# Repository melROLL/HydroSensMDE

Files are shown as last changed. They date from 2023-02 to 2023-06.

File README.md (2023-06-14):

# HydroSensMDE

## The TEAM
the team is composed of : Joshua, Tristan, Nicolas and Melvyn

## The Software 
You can download the realease folder in order to have the .exe file for windows and find as well the instruction manual.
all the source code is provided in the technical part if you need or want to compile it for other operating system. 

### user interface 

<p align="center">
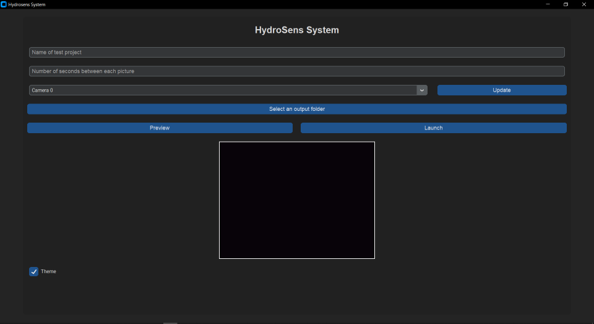
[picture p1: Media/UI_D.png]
  
</p>

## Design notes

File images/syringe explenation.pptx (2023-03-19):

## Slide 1

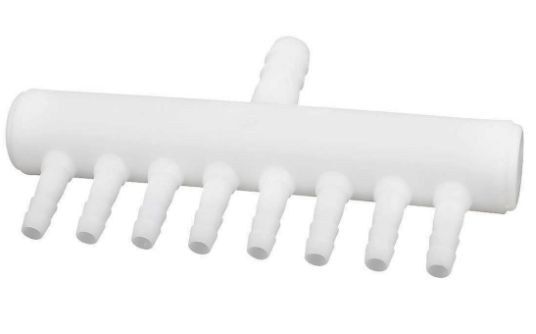
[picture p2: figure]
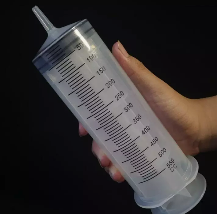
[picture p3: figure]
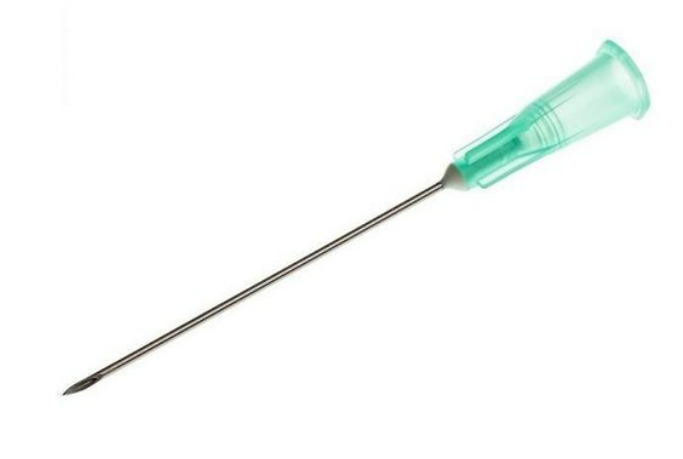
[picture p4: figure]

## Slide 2

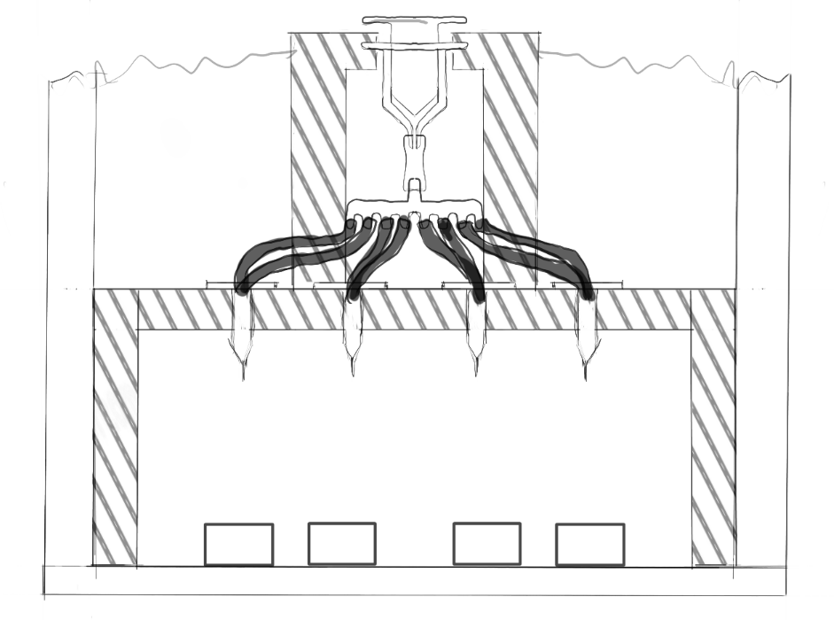
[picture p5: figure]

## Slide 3

product | qty | price
big syringe | 1 | 8,01
tube | 20 cm | 1,99
tubesplitter | 1 | 9,94
syringe needles | 10 | 5,28
wood | scrapwood from school
filament | leftover from the photobox
screws | leftover from the photobox
total | | 25,22

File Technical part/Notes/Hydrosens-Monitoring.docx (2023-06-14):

# Fourth-year project

Participants:

- Joshua GROEN
- Tristan MICHELENA
- Melvyn ROLLAND
- Nicolas WATTENHOFFER

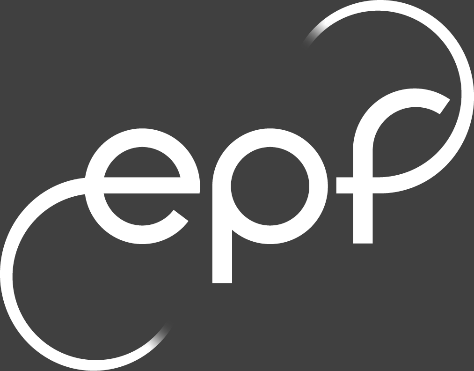
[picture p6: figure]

# Management monitoring

## Context

The client Ms. Mouton makes a lot of experiments testing different products from her subject study. She follows a protocol, and she takes pictures of the results. She visualizes the absorption of the water on a treat piece of paper regarding the duration. The point is today, everything is made by hand. These experiments require a lot of precious time of Ms. Mouton. The main point of this project is to automatize these steps following the same protocol. The project is spliced in two parts. The first part concerns the physical tools necessary to automatically take pictures in repeatable environment. The second part treats the development of the software to detect when the product fails.

## Objectives

Criteria of Ms. Mouton:

- Easy user interface
- Time saving.

Criteria for the consistency and the usage of the project:

- Make the experiment repeatable, same samples, same results:
  - Same environment
  - Fixed position of the camera and same lighting condition
  - Fixed position of the sample
- Usage guide

Functionalities:

1. Acquire picture every defined time.
2. Once the absorption is detected:
a. Visualize experiment result: at which time absorption occurred.
b. Visualize the flow rate of absorption.
3. Store the results.

## Management tools

- Github
- Teams
- Roadmap and Backlog

## First meeting – Story mapping 02/02/2023.

1. Understand the project of the client.
2. Understand the need of the client.
3. The steps of the project: Design a prototype, create a data processing tool, test and improve.
4. Create something simple of usage.
5. Functionalities:
  - Data output: absorption or not, amount of water, time at which absorption occurred, flow rate.
  - Let the user choose the duration between pictures.
  - Export a csv file with results.
  - Stop the experiment when all samples absorbed.
6. To contact Ms. Mouton, use Teams or in face to face at school.

## Second meeting – Monitoring 02/10/2023.

1. Budget:
- Camera 2k: over 15€
- Use the camera giving but the teacher, Logitech 720p.
- Light: circular light or led -> we can test both.
- Check for wood if we build the box or buy a folding box.
- A budget can be assigned by the school.
2. The box:
- Number of samples: between 4-8 samples.
- Looking for a hydrophobic floor.
3. Program:
- Add a name for the folder of each experiment.

Third meeting – Monitoring 02/17/2023.

We had a meeting without the client Ms. Mouton.

We have decided to share our files via github and we practiced using it. We concluded that we should buy as soon as possible everything we need, and we also have a camera from Mr. Gademer.

To do for next time:

- Create the list of tasks regarding the roadmap.
- Search ideas for the floor box.
- Ask Cyril Durant if we can get the wood to establish the budget.
- Presentation: Why do we want to build the box ourselves? And the budget.
- Create a report of last week meeting.
- Create the list of tasks regarding the roadmap.

## Fourth meeting – Monitoring 02/24/2023.

News

How to put water droplets on all the samples on the same time? (With an acceptable delay of 10 seconds).

According to the meeting this morning. We will reduce the number of samples to a maximum of 4. Indeed, the amount of water put on the paper is very precise and need a pipette to be realized.

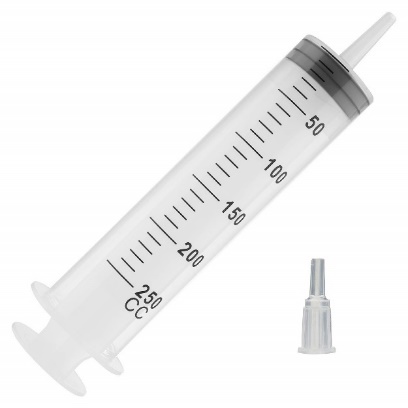
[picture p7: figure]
250ml Syringe, Extra Large Plastic Syringes for Glue Dispensing, Scientific Labs, Watering, Refilling, Multiple Uses: Amazon.com: Industrial & Scientific

In a second time we can think about a system which can facilitate the experiment’s process. The two possibilities are the software method, in other words put sample one after the other. Second possibility, to create an easy-to-use support as showed by the following pictures:

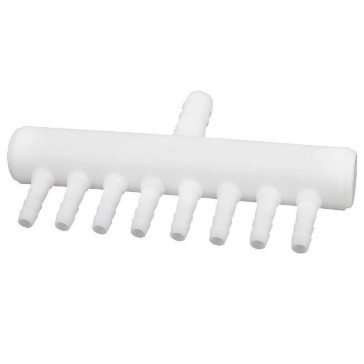
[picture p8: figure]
Plastic 8-Way Aquarium Tube Splitter Air Valve - Walmart.com
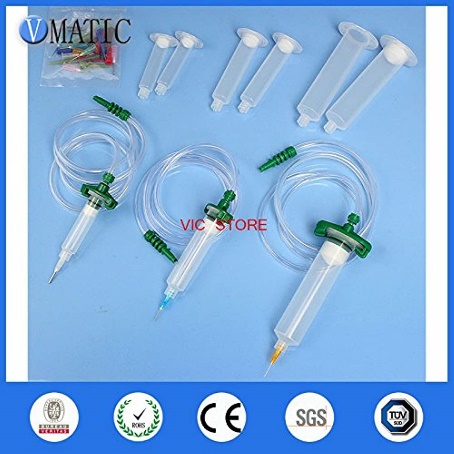
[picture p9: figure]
Liquid Dispensing Adhesive Glue Plastic Pneumatic Syringe + Dispenser Syringe Adapter Fitting Valve 5/10/30 Cc Ml + Syringe Needles: Amazon.com: Industrial & Scientific

We propose two possibilities for the floor of the box:

- Plastic cotenant, to buy.
- Acrylic panel, to build.

Decisions

We will make the box by ourselves with wood.

To do in a short term:

Ask Cyril Durant for the wood to start the construction of the box.

The next meeting will take place the 03/10/2023 at 9:45 a.m., if we don’t have enough news, we can push the meeting for the next week.

## Fifth meeting – Monitoring 03/10/2023.

### Management meeting

1. The road map.

The road map’s big steps must include a title that represents a deliverable. It’s important to precise that dates are just hypothetical because it’s almost impossible to have a vision of the work so early in the project.

2. Backlog

The tool must be shared with all the participants of the project to make it dynamic. We must create a Kanban board to visualize the progress of the work.

Example:

Backlog | To do | Doing | Done
Box | | | Get the wood
| Cut the wood

The main purpose of the Kanban is to update it every week to highlight the progress compared to the previous meeting. It also involves the client in the monitoring of the tasks.

### Client meeting

1. The water drop solution:

It can resolve the issue; Ms. Mouton will check for materials that allow to implement the solution in the lab.

In all the cases, it’s not an expensive solution. We can test the implementation of the solution.

2. Sample of pictures

Picture name = Number of carbon chain – Dilution – minutes (example= C12-5-2)

3. Fully transparency box

The documentation must be understandable for everyone who don’t know anything about the project with a granularity of the construction of the box, for the physical part. The code will be commented and detailed about the functions for any other people who want to discover it.

The next meeting will take place the 03/24/2023 at 9:45 a.m., if we don’t have enough news, we can push the meeting for the next week.

## Sixth meeting – Monitoring 03/24/2023.

### Management meeting

The roadmap is now well, the previous errors have been corrected. For big changes, it is important to keep the previous version of the roadmap to visualize the difference between the original basis and the actual basis.

More details about the user stories have been given, the user stories are kind of functionalities that have been implemented. The granularity is between the goal of the sprint and the technical tasks.

We are using two different sharing tools, the first one, the kanban model for the customer and the second one, for the teams. This solution is great, the information shared between the team members is not the same that the information shared this the client. However, the tool used by the team members must be more detailed in the planification.

The kanban model must include only the ToDo of the sprint. The point here is to show at the end of the sprint that the defined ToDo at the beginning of the sprint have been made.

### Client meeting

1. Drop water system.

The products to try the water droplets dispenser are ordered and will arrive around the sixth of April. And the precision pipet is in Ms. Mouton office so we can try it.

2. Light.

First, the team want to use strip led. The solution is easier to implement and is also cheaper than a light bulb.

Second, we must check the available part at school and if there is nothing that can help use, Ms. Mouton will buy the article we will propose her.

The next meeting will be the mid-term meeting and will take place the 04/07/2023 at 12:15 a.m.

## Midterm Presentation – Monitoring 04/07/2023.

Feedback and global remark on the project’s organization and work.

Remark

Clear idea visually of project in the beginning

Faced challenges:

- How managed?
- how did we go managed?

Density of pixels different between position?

Different success criteria: not fix.

Consistance of schéma

Use Consistancy to explain where we are:

Show itérative : Validation

Doubt water dop dispenser

## Seventh meeting – Monitoring 04/14/2023.

### Management meeting

The organization of the sprint is now established thanks to the Github project’s tool. It allows to follow all the tasks that must be done during the sprint and to share it with the client. So, this last can follow the advancement of the work.

However, this tool is great for the delivery process and the communication with the client, but we need something else to share the experience team members. Which means how each participant of the work feel about the project. One of the ways to get this feedback is based on emotions. How do I feel working on this project? Am I very motivated or maybe I am disappointed? These feedbacks allow to manage the motivation of the team and to create bands between participants. It is a part of the agile method. This process has nothing to see with the delivery process. For the next meeting, the group must find a way to collect and manage these feedbacks.

The next meeting will be the eighth meeting and will take place the 05/12/2023 at 8:45 a.m.

Joshua GROEN - Tristan MICHELENA - Melvyn ROLLAND - Nicolas WATTENHOFFER 4A Project

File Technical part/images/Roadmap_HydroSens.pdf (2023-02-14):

# Hydrosens

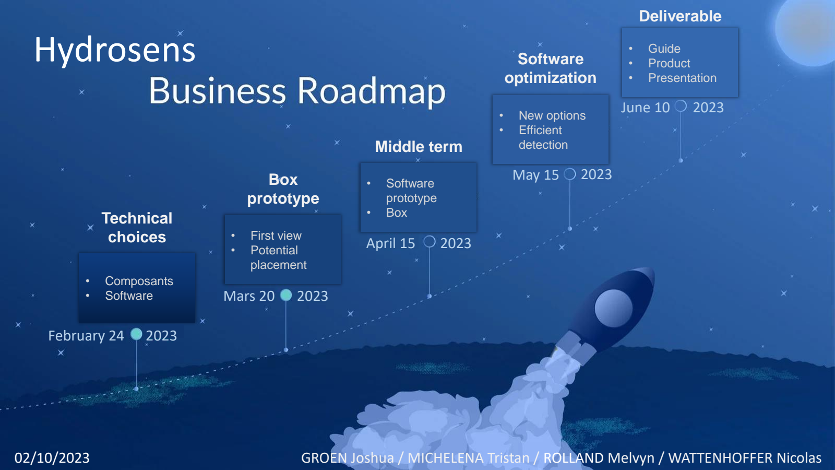
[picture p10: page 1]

- Composants
- Software
- First view
- Potential
placement
- Software
prototype
- Box
- New options
- Efficient
detection
- Guide
- Product
- Presentation
February 24 | 2023
Mars 20 | 2023
April 15 | 2023
May 15 | 2023
June 10 | 2023

Deliverable

Technical
choices

Box
prototype

Middle term

Software
optimization
02/10/2023 | GROEN Joshua / MICHELENA Tristan / ROLLAND Melvyn / WATTENHOFFER Nicolas

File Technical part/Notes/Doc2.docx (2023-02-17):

03/02/2023 meeting with a seminar

During this meeting we discussed what we need to do from the perspective of project manager

We decided to explore how we can make the photo box and present multiple ways to make the box to Julia. In order to make sure we are on the same page and know how to continue.

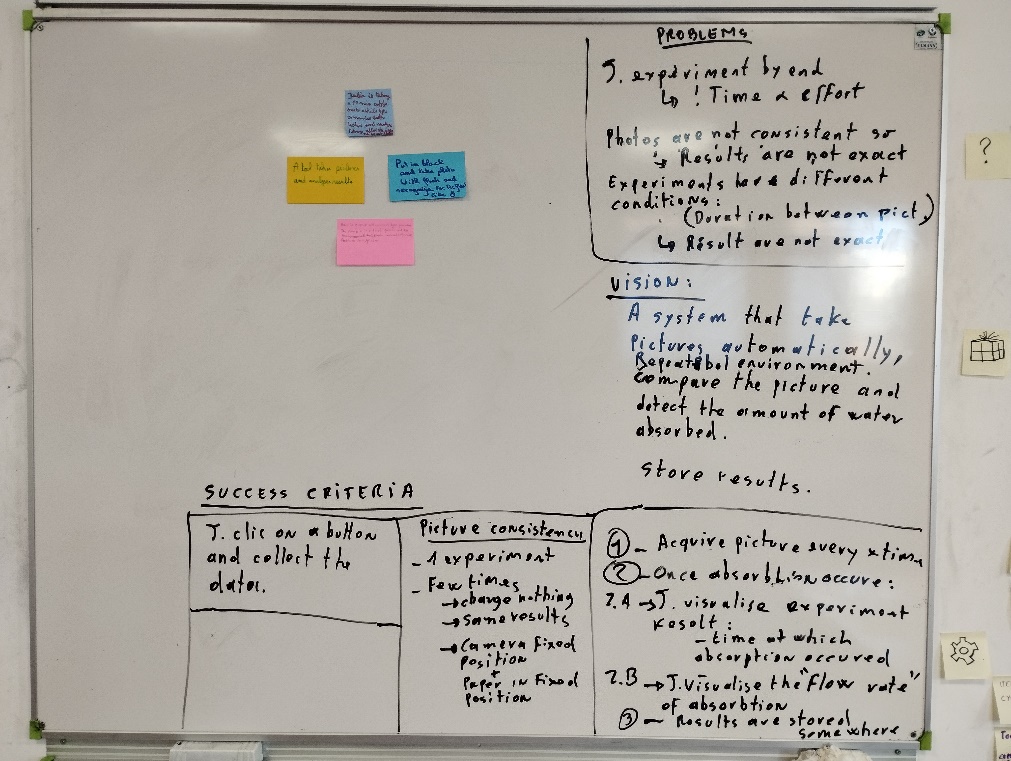
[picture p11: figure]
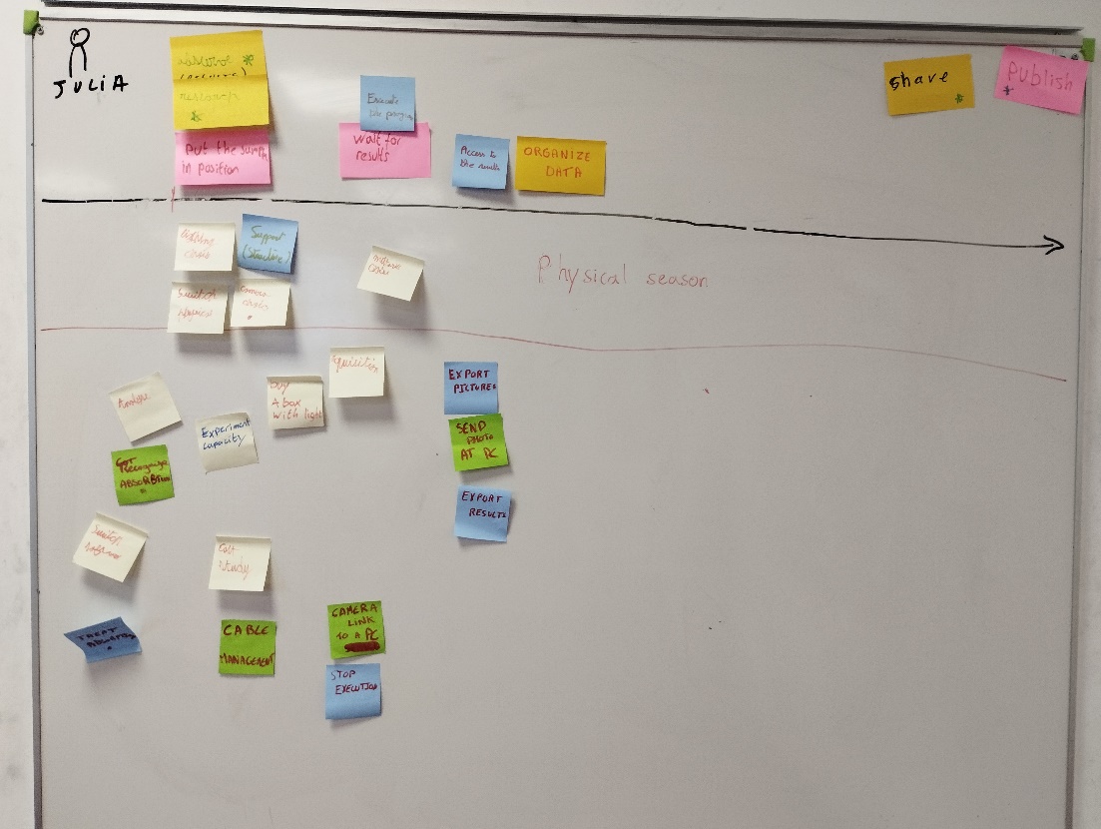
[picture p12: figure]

10/02/2023

We showed our presentation to Julia and came to the conclusion that we have to show her a complete budget of everything we need.

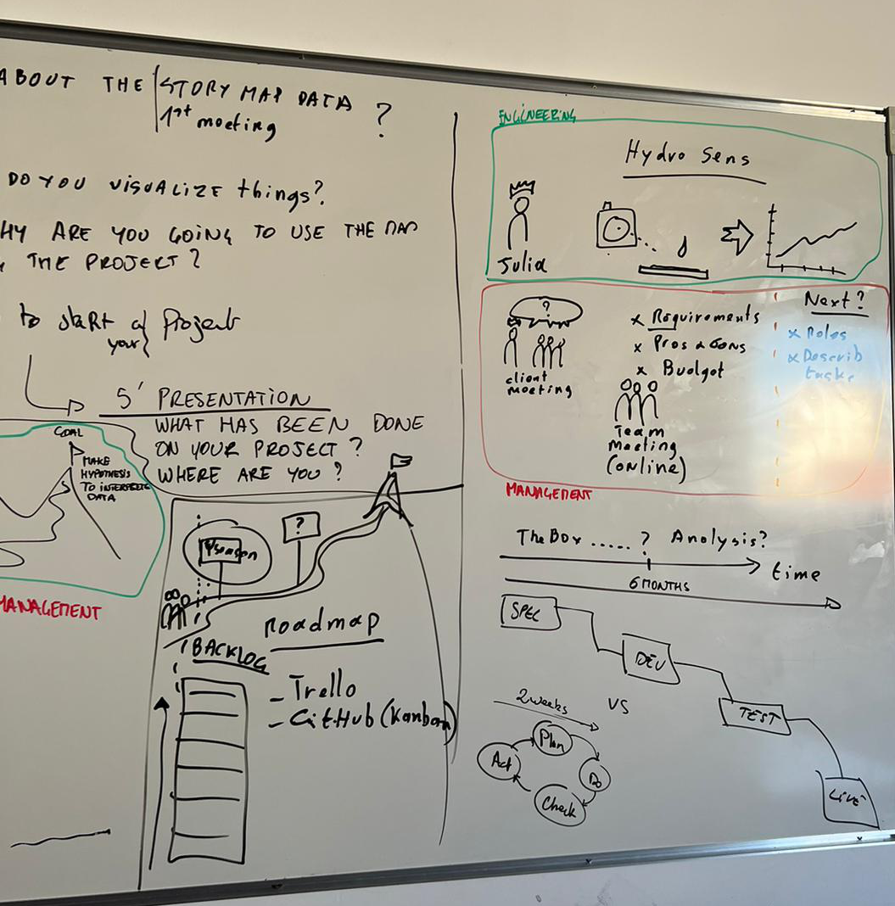
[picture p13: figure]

what we need:

- Argue why we want to make the box ourselves or not
- Create a budget
- Share our notes with everyone involved

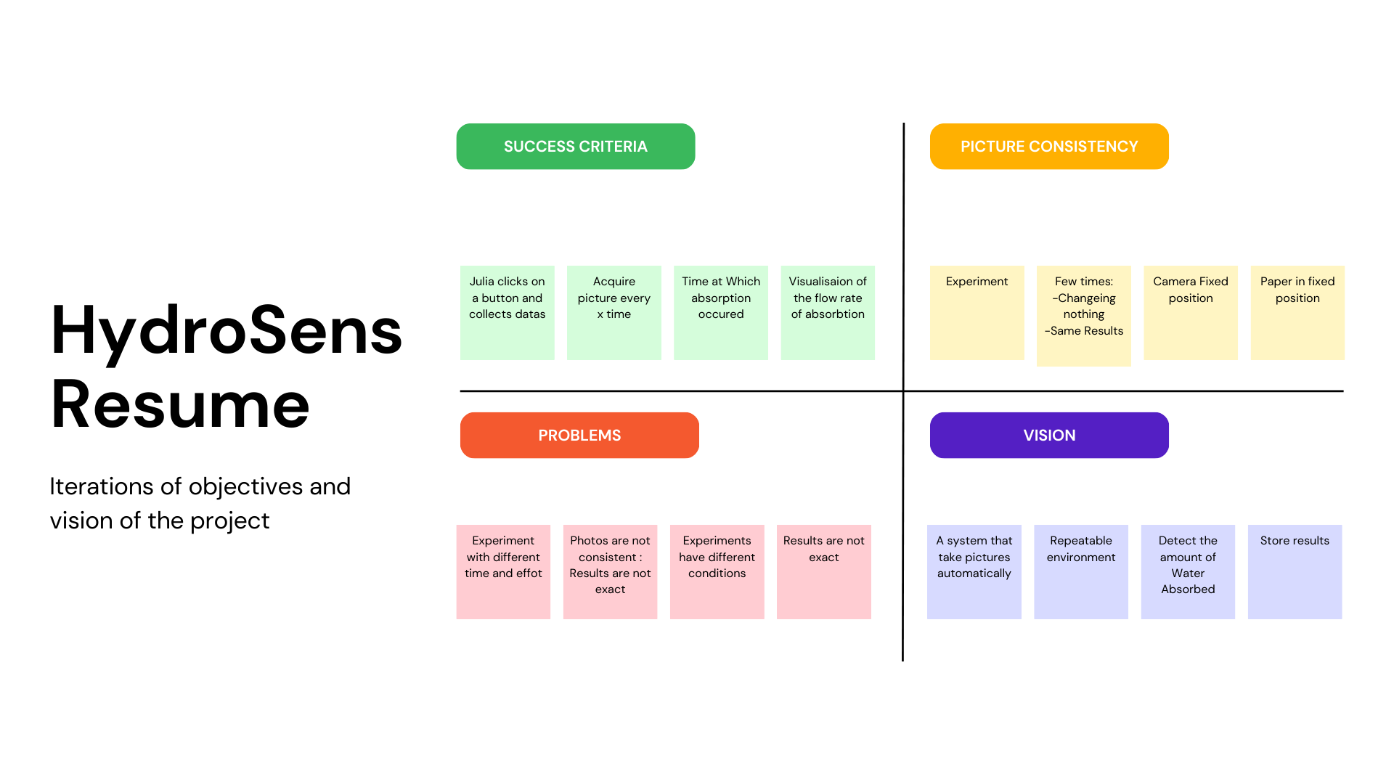
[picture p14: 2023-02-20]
Technical part/images/HydroSens_Resume.png

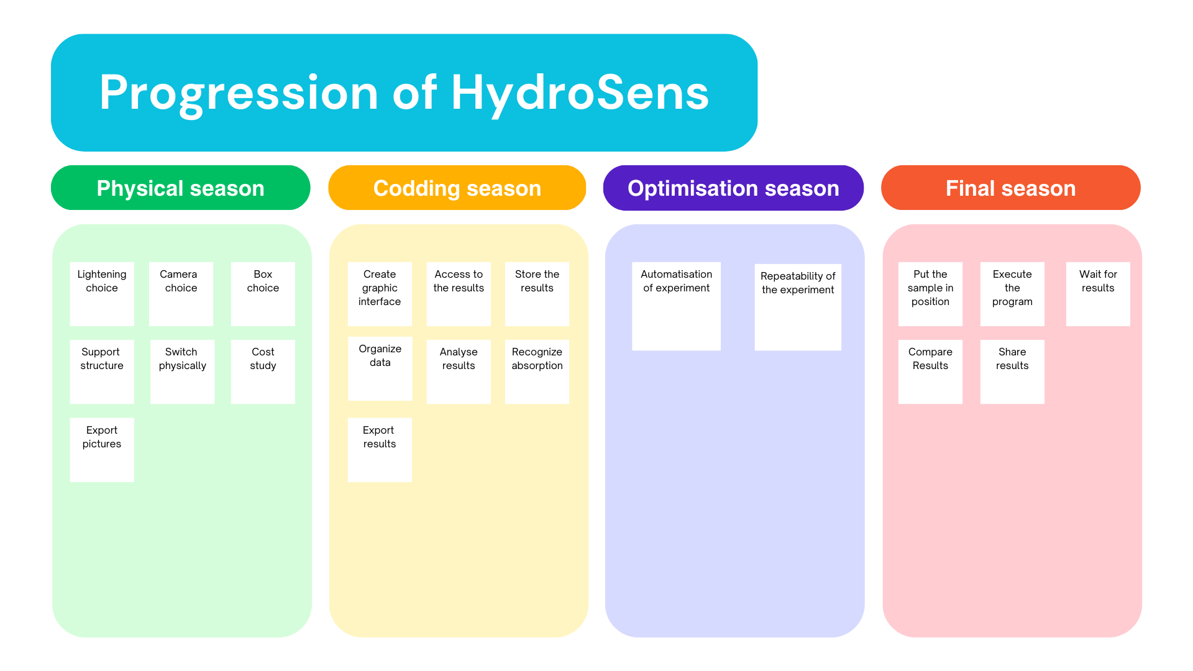
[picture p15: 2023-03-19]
Technical part/images/Plan.png

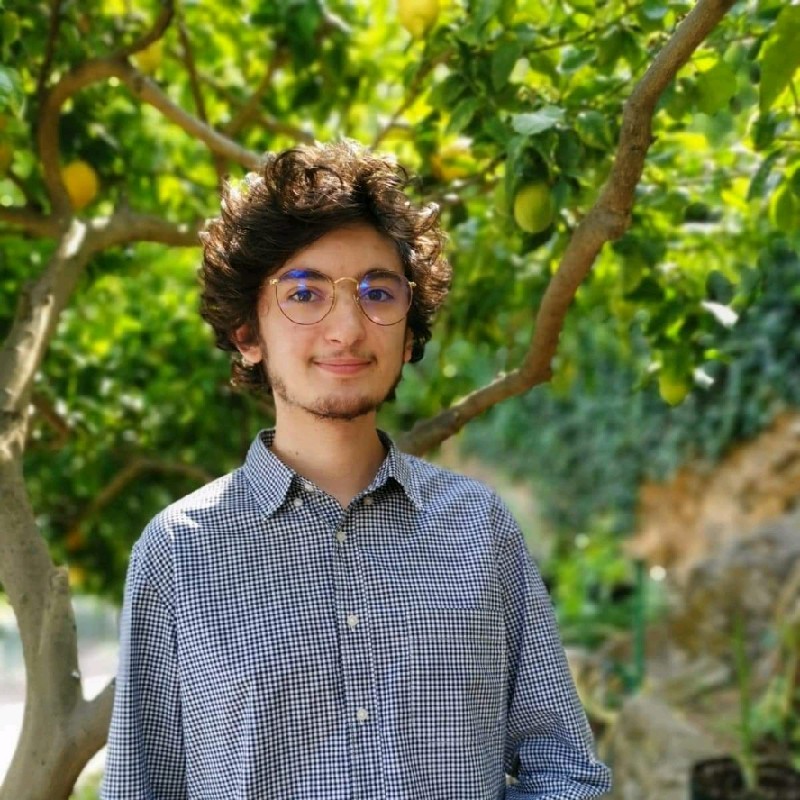
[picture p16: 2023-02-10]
Media/melvyn.jpg

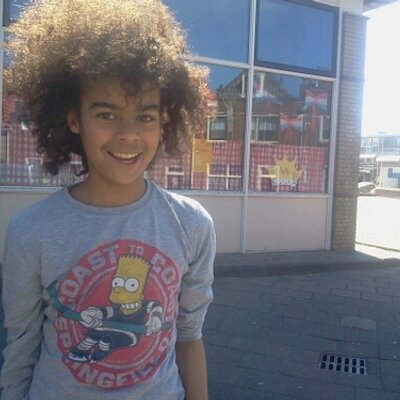
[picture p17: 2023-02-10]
Media/joshua.jpeg

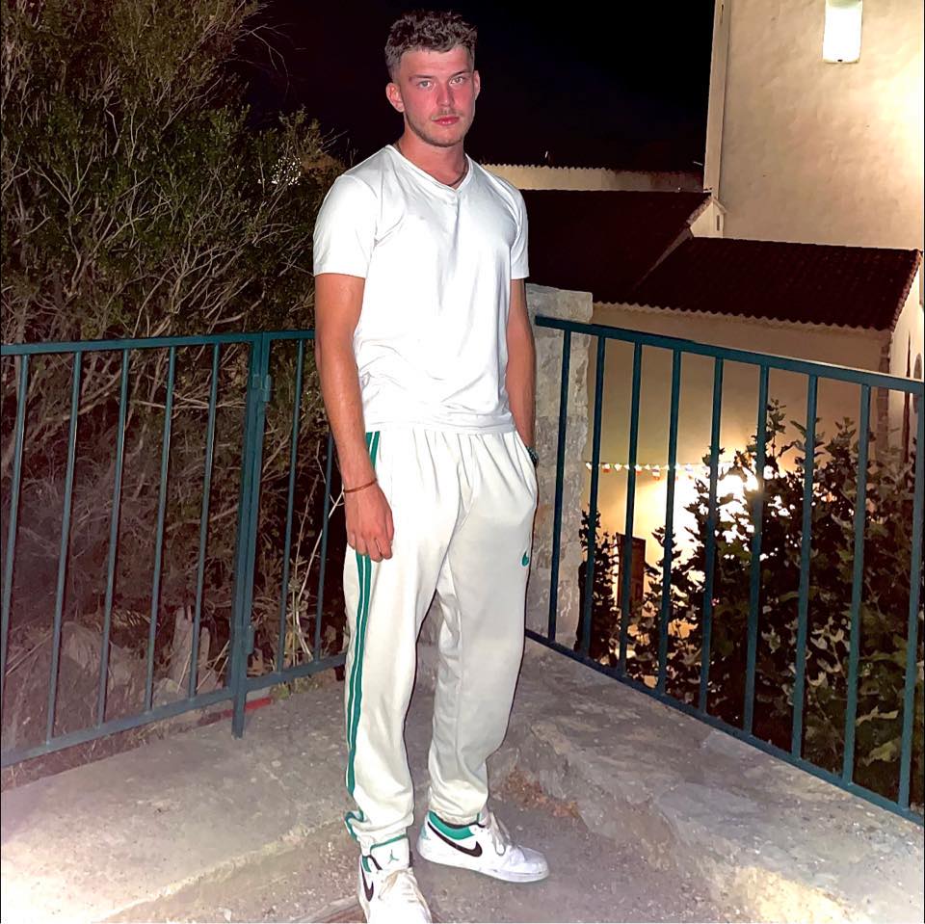
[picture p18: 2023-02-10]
Media/Melvyn2.jpg

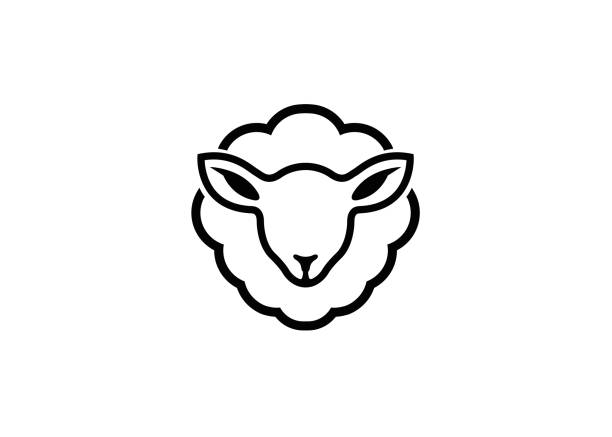
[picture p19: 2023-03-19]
Technical part/PhotoBox/Pictures_for_laser_engraver/Mouton.jpg

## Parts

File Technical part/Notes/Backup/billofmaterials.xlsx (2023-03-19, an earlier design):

Bill of materials complete prototype |  |  |  |  | Bill of material Photobox
Products/ materials | QTY | Price 1 | Price 2 | Link | Products/ materials | QTY | Price 1 | Price 2 | Link
Selfmade photobox | 1 | 10 | 39.95 |  | triplex wood | - | - | -
Premade Photobox1 | 1 | 59 | - | https://www.adorama.com/golst40.html?sterm=1jDRDPy2VxyNU%3Ae3n50BGQccUkAylOX9N2mHUs0 | screws | 5
Premade Photobox2 | 1 | - | - |  | glue | 5
Led strip | 1 m | 1.13 | - | https://campaign.aliexpress.com/wow/gcp/tesla-pc-new/index?UTABTest=aliabtest377151_530968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 | reflective spraypaint | - | 29.95 | - | https://www.handyhomeottevaere.be/fr/notre-gamme/decoration-57722/peintures-techniques-57740/peintures-de-marquage-57743/albedo-100-spray-reflechissant-perman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
Influencerlight | 1 | 10.4 | - | https://campaign.aliexpress.com/wow/gcp/tesla-pc-new/index?UTABTest=aliabtest377151_530968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 | total | 39.95
Camera 1 | 1 | 17 | -
Camera 2 | 1 | 35 | -
Filament | 1 kg | 0 | 15 | -
3d print inserts | 10 | 8.59 | - | https://www.amazon.fr/STCRERAG-Assortiment-Anti-oxydation-Anti-corrosion-Anti-d%C3%A9formation/dp/B095VW7GBW?hvadid=543211283163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 | -
Plastic containers | 8 | 8.04 | - | https://www.pandahall.com/selected-p-2266392-benecreat-15-pack-high-transparency-1-96x1-96x0-78-plastic-storage-containers-mini-earplugs-storage-box-for-bead-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 | -
Price with selfmade box | 44.76
Price without selfmade box | 85.72

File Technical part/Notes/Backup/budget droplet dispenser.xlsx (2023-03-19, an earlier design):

product | qty | price | link
big syringe | 1 | 8.01 | https://www.aliexpress.com/p/trade/confirm.html?objectId=1005002526934825&skuAttr=&skuId=12000028938137084&quantity=1
tube | 20 cm | 1.99 | https://www.moddiy.com/products/High-Quality-Food-Grade-Flexible-Silicone-Tubing-(8mm-ID-x-10mm-OD).html
tubesplitter | 1 | 9.94 | https://www.fruugo.fr/plastic-8-way-aquarium-tube-splitter-air-valve/p-111755172-235748253?language=en&ac=ProductCasterAPI
syringe needles | 10 | 5.28 | https://www.degros.nl/fr/aiguilles-bd-injection-18g-rose-12x40mm-100-pieces.html
wood | scrapwood from school
filament | leftover from the photobox
screws | leftover from the photobox
total |  | 25.22

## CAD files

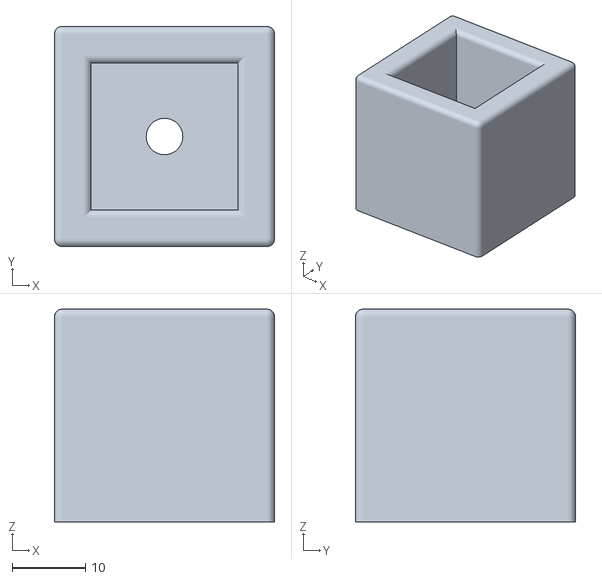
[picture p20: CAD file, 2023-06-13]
Releases/photobox/leg.stl
30.0 x 30.0 x 29.0

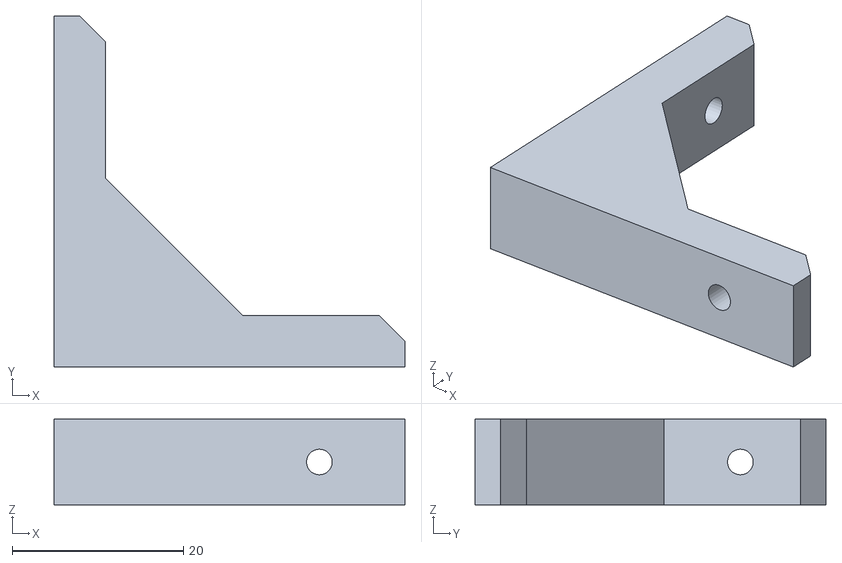
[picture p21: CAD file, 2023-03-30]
Technical part/PhotoBox/CAD_Modeling/6mm/L joint V2.stl
41.0 x 41.0 x 10.0

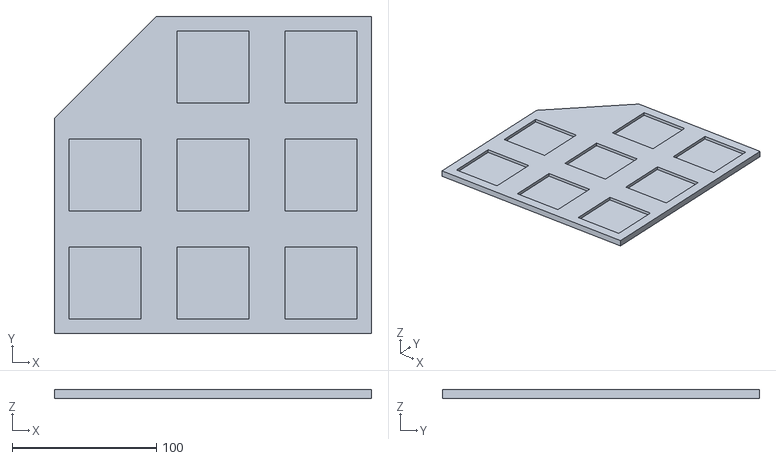
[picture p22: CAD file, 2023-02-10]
Technical part/PhotoBox/CAD_Modeling/7mm/Tray.stl
220.0 x 220.0 x 6.00

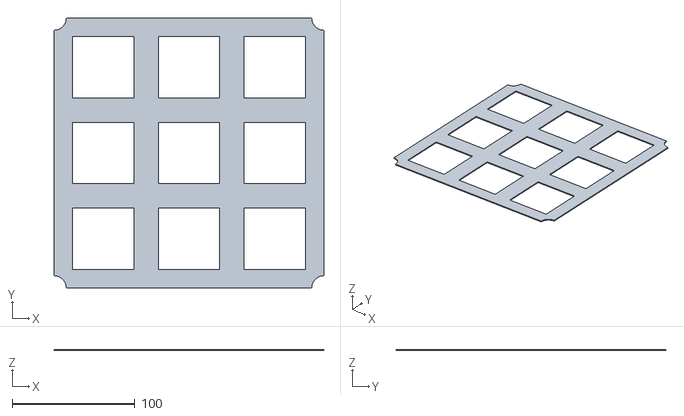
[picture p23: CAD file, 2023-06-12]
Releases/photobox/grid.stl
220.0 x 220.0 x 1.00

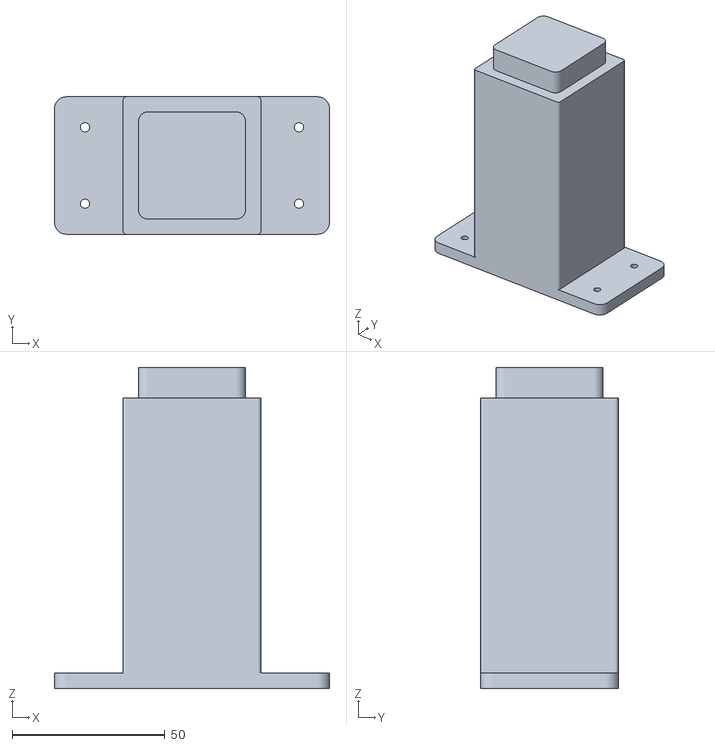
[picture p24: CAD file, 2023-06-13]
Technical part/droplet dispenser/splitter holder.stl
90.0 x 45.0 x 105.0

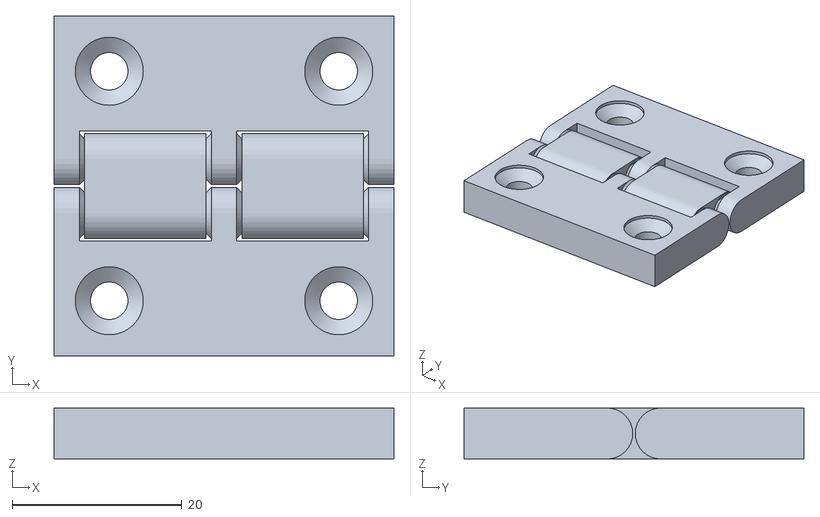
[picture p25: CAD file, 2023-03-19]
Technical part/PhotoBox/CAD_Modeling/6mm/reversible_hinge_with_holes.stl
40.0 x 40.0 x 6.00

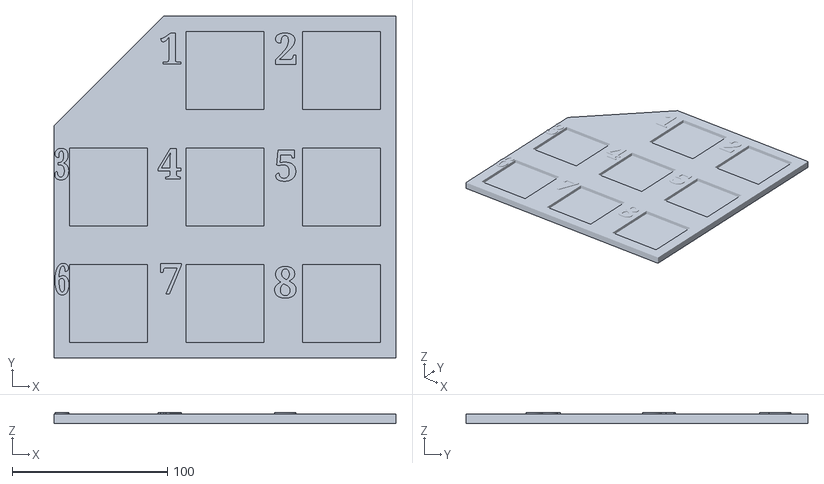
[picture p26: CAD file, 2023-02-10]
Technical part/PhotoBox/CAD_Modeling/7mm/TrayWithNumbers.stl
220.0 x 220.0 x 7.00

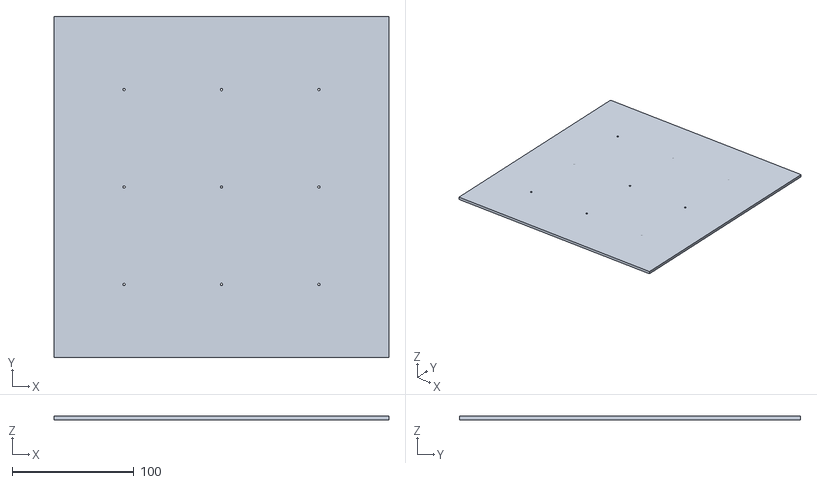
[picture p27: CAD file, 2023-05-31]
Releases/photobox/plane1-Body.stl
275.0 x 280.0 x 3.00

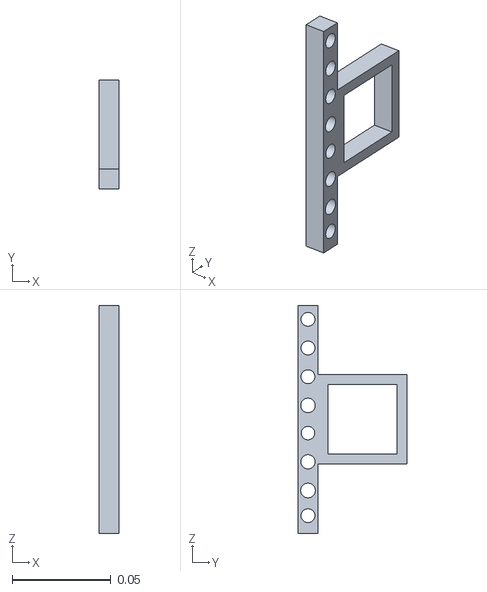
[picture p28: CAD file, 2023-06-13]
Technical part/droplet dispenser/splitholdframe.stl
0.01 x 0.055 x 0.115

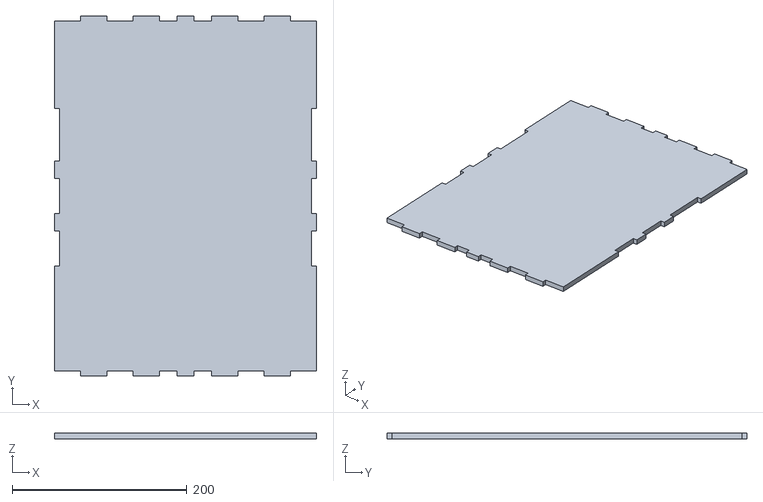
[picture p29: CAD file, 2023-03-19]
Technical part/PhotoBox/CAD_Modeling/6mm/back.stl
300.0 x 412.0 x 7.00

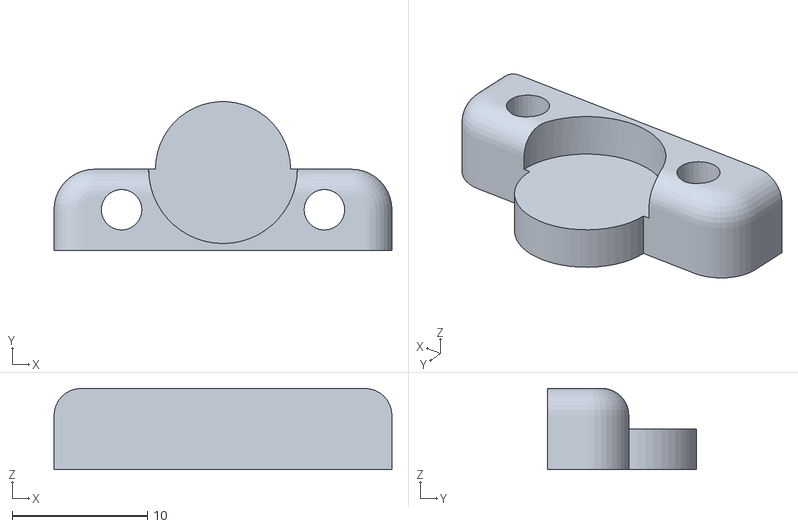
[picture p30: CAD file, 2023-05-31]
Releases/photobox/magnetholder2.stl
25.0 x 11.0 x 6.00

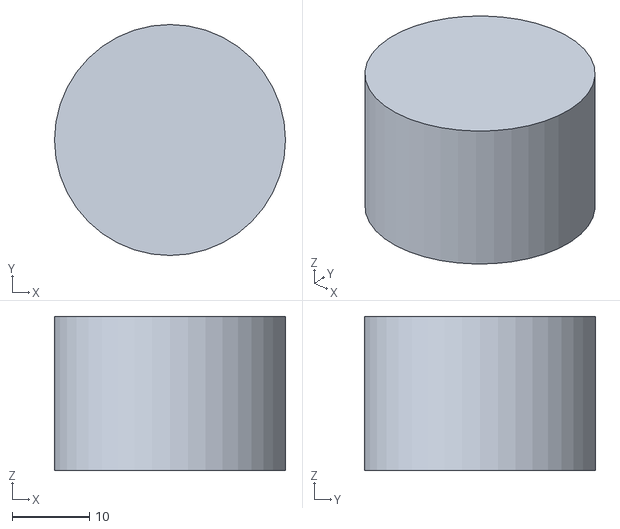
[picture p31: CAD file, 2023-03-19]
Technical part/PhotoBox/CAD_Modeling/6mm/foot.stl
30.0 x 30.0 x 20.0

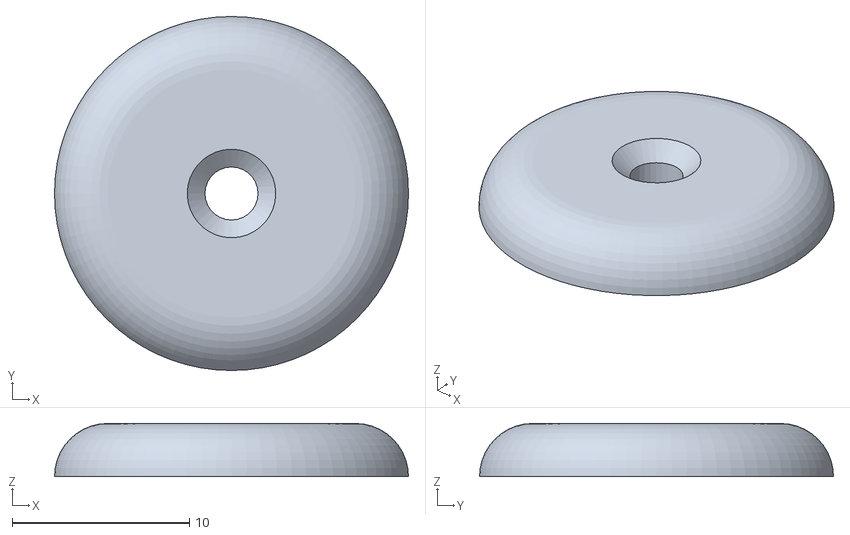
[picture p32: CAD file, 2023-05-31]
Technical part/PhotoBox/CAD_Modeling/Sac_Poubelle_Retainer_bigger.stl
20.0 x 20.0 x 3.00

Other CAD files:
Releases/photobox/Door.stl
Releases/photobox/Sac_Poubelle_Retainer.stl
Releases/photobox/Side.stl
Releases/photobox/Top.stl
Releases/photobox/Webcam_Connector.stl
Releases/photobox/base.stl
Releases/photobox/feet-BodyPad.stl
Releases/photobox/magnetholder1.stl
Releases/photobox/plane2 - Copy-BodyPad.stl
Technical part/PhotoBox/CAD_Modeling/6mm/Door.stl
Technical part/PhotoBox/CAD_Modeling/6mm/L joint.stl
Technical part/PhotoBox/CAD_Modeling/6mm/Side.stl
Technical part/PhotoBox/CAD_Modeling/6mm/Top.stl
Technical part/PhotoBox/CAD_Modeling/6mm/base.stl
Technical part/PhotoBox/CAD_Modeling/Sac_Poubelle_Retainer.stl
Technical part/PhotoBox/CAD_Modeling/Webcam_Connector.stl
Technical part/PhotoBox/CAD_Modeling/feet-BodyPad.stl
Technical part/PhotoBox/CAD_Modeling/magnetholder1.stl
Technical part/PhotoBox/CAD_Modeling/paper holder taged 1.stl
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

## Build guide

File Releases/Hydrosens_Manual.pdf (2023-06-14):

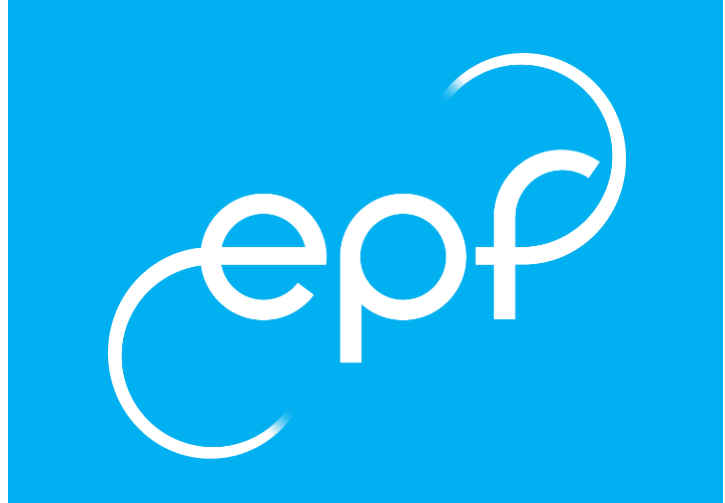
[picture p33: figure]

# Hydrosens Manual

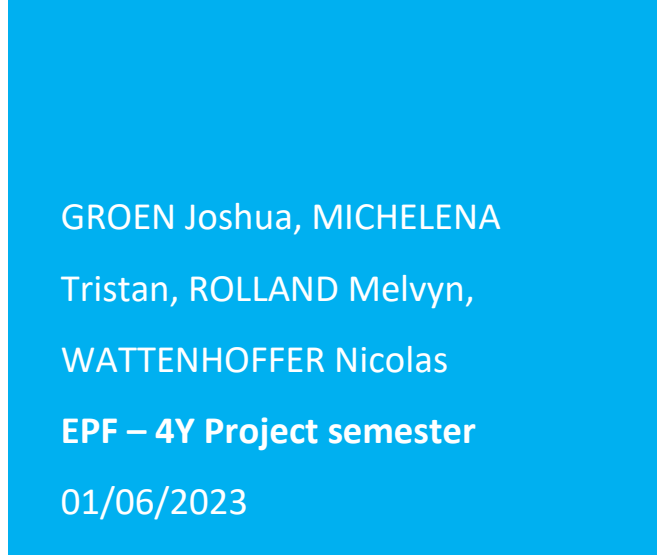
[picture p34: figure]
GROEN Joshua, MICHELENA; Tristan, ROLLAND Melvyn,; WATTENHOFFER Nicolas; EPF – 4Y Project semester

GROEN JOSHUA, MICHELENA TRISTAN, ROLLAND MELVYN,
WATTENHOFFER NICOLAS | 1

HYDROSENS MANUAL

## Table of content

Introduction | 2
List of parts and how to make them: | 3
Laser cuted: | 3
3D printed: | 4
Other parts | 5
Box Assembly | 6
How to setup the software | 8
How to prepare the samples | 9
How to use the software | 10
Conclusion | 11

GROEN JOSHUA, MICHELENA TRISTAN, ROLLAND MELVYN,

## Introduction

Hydrosens is a project ordered by Julia Mouton and executed by Groen Joshua, Michelena Tristan,

Rolland Melvyn and Wattenhoffen Nicolas. The objective of this project is to automate the procedure of

capturing images of small paper fragments adorned with water droplets and subsequently analyzing them

to ascertain whether water has been absorbed. The purpose is to enhance efficiency, accuracy, and

consistency by enabling the experiment to be replicated, thereby saving time, and yielding more precise

and reliable outcomes. In this manual you can find how to make, install and to use the photobox as well

as the software that comes with it. Hydrosens is an opensource project feel free to share it.

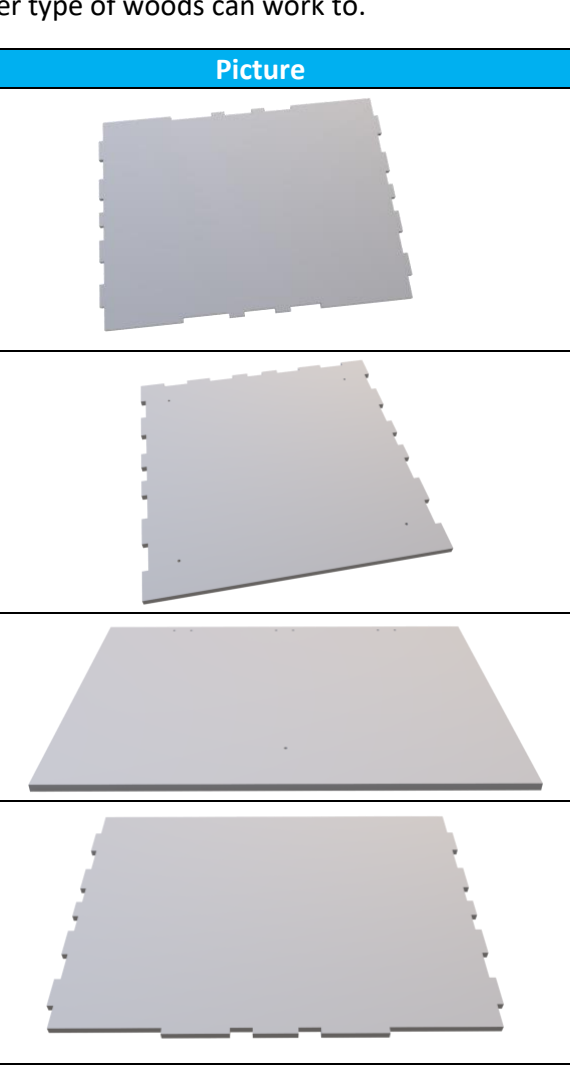
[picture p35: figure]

GROEN JOSHUA, MICHELENA TRISTAN, ROLLAND MELVYN,

## List of parts and how to make them:

### Laser cut:

The biggest part that needs to be cut is 300mm X 420mm. Check if your laser cutter is big enough before cutting it.

There is two set of files one for 7mm wood thickness and the other for 6mm wood thickness.

We advise to use MDF but plywood and other type of woods can work to.

Name | Quantity | Picture
Back | 1
Base | 2
Door | 1
Side | 2

GROEN JOSHUA, MICHELENA TRISTAN, ROLLAND MELVYN,

### 3D printed:

The biggest part that needs to be printed is 220mm X 220mm. Check if your printer is big enough before printing it.

All parts are printed using PLA because it is an easy to print material and its ecological impact is better than other thermoplastics.

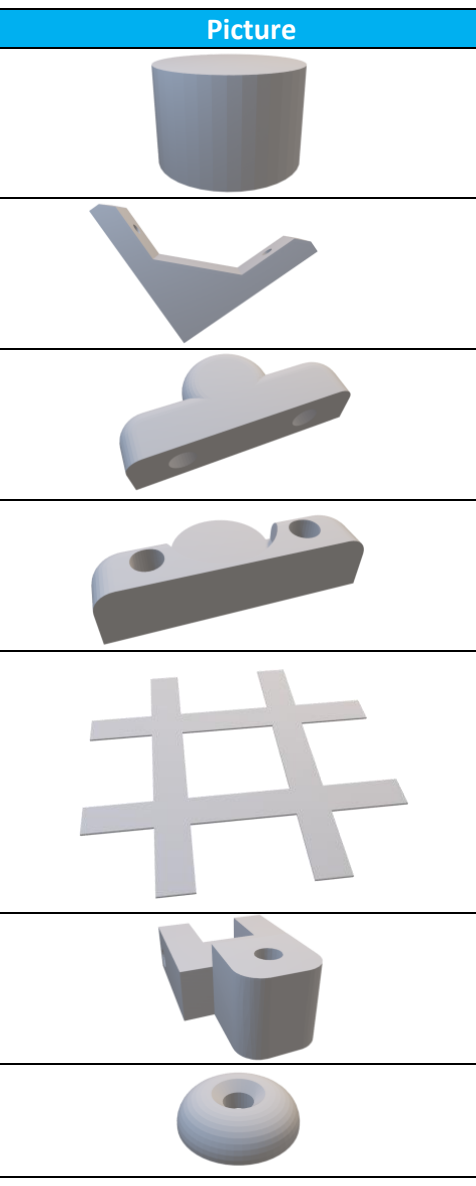
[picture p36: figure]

Name | Quantity | Picture
Foot | 4
L Joint | 2
Magnet holder1 | 1
Magnet holder 2 | 1
Grid | 1
Webcam_Connector | 1
Thrash_Bag_Holder | 4
Hinge_cale | 3

Recommended settings are a layer height of 0.2 mm and an infill of 15%.

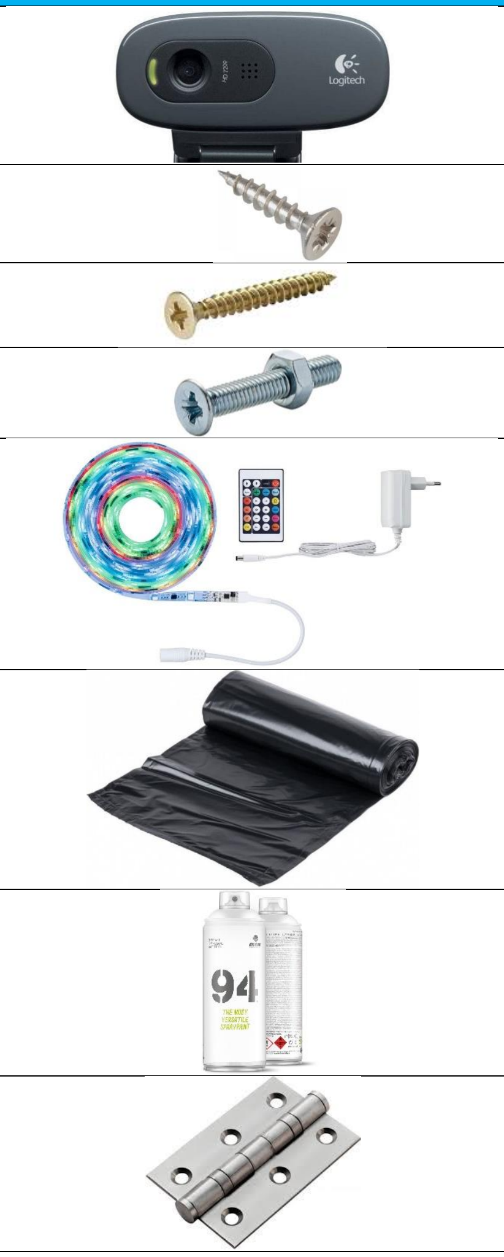
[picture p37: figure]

GROEN JOSHUA, MICHELENA TRISTAN, ROLLAND MELVYN,

### Other parts

Name | Quantity | Picture
Webcam Logitech C270 | 1
3mm*10mm Wood screw | 16
3mm*20mm Wood screw | 4
M2 bolt and nut 2mm | 1
Led Strip | 1
Trash bag | 1
Acrylic white paint | 1
Hinge | 3

Be careful to note that the remote of the led strip uses a cr2025 battery.

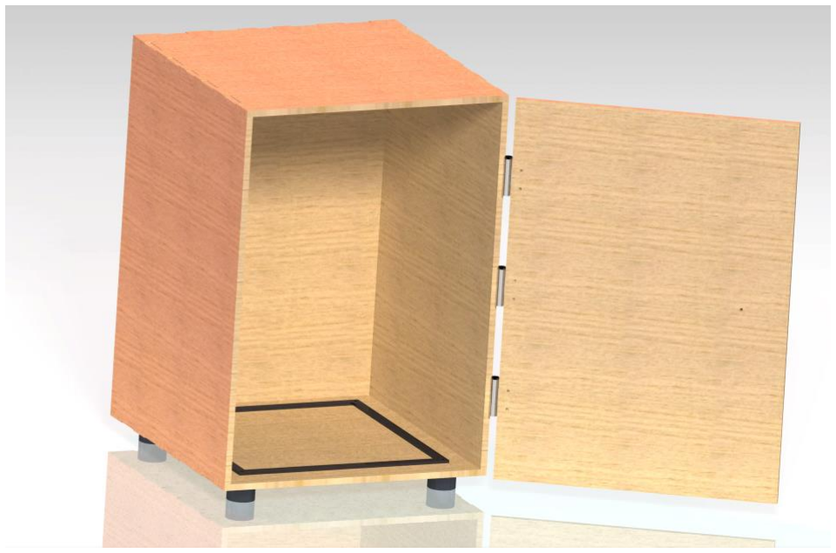
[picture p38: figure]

GROEN JOSHUA, MICHELENA TRISTAN, ROLLAND MELVYN,

## Box Assembly

To assemble the box, it is necessary to have all the parts pre-cut and printed in advance.

Render of the assembled box: keep in mind that there may be variations or discrepancies between this representation and the actual physical model.

Here are the complete instructions for assembling the box:

First paint the interior of the box in white.

Gather the following items: base, 4 Foots, 4 screws, 4 Trash_Bag_Holders, 2 L-shaped brackets, wood glue, box back, 3 hinges, 3 hinge shims, 12 screws, door, magnet holder 1 and 2, magnet, webcam, new webcam support, LED strip.

1 - Place the Trash bag on the base.

2 - Insert a Trash bag holder into a 3mm screw.

3 - Insert the screw with the holder into one of the 4 pre-made holes in the corners, piercing the garbage bag.

4 - Once done, screw a Foot onto the end of the screw.

5 - Repeat steps 3 to 5 three more times, using the remaining 3 screws, Trash_Bag_Holders, and Foot.

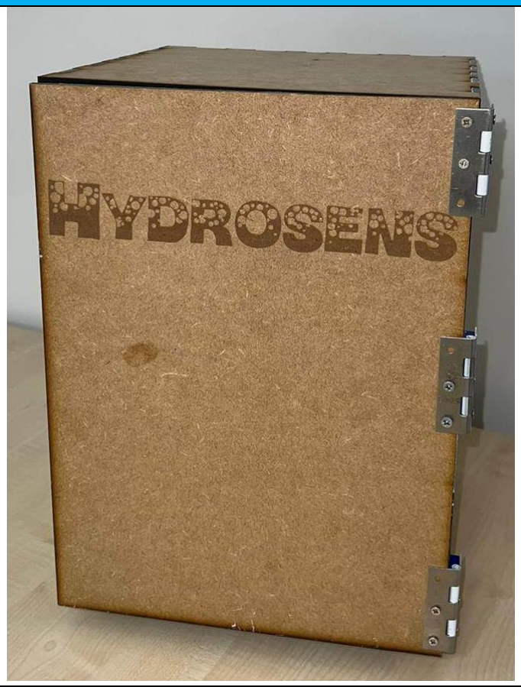
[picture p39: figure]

GROEN JOSHUA, MICHELENA TRISTAN, ROLLAND MELVYN,

6 - Take one side of the assembled box and attach it to the base by screwing the two L-shaped brackets in a way that they hold the base and sides together.

7 - Apply wood glue where the pieces meet.

8 - Assemble the box back while applying glue.

9 - On one side, screw the 3 hinges using the hinge shims. Use the provided 12 screws.

10 - Screw the door onto the hinges.

11 - Screw magnet holder 2 onto the door, placing a magnet inside.

12 - Screw magnet holder 1 onto the side, inserting a magnet inside.

13 - Next, take the webcam, remove its support, and attach the new webcam support by screwing it onto the top of the box.

14 - Glue the LED strip onto the top of the box.

15 - Once the top of the box is assembled, position it onto the box.

These instructions will guide you through the complete assembly of the box, following the specific steps.

Here are the results of what you should have:

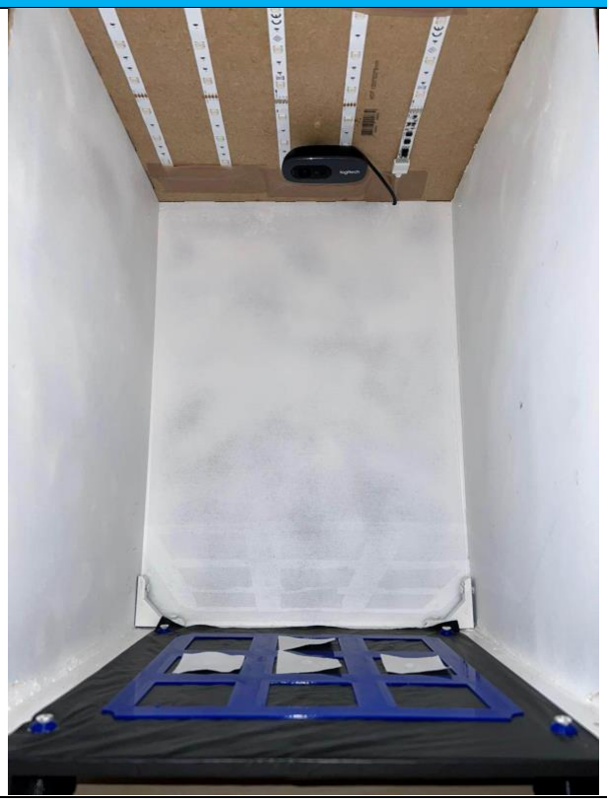
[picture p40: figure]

Assembled Box Outside | Assembled Box Inside

GROEN JOSHUA, MICHELENA TRISTAN, ROLLAND MELVYN,

## How to setup the software

The software has been developed to run on a windows computer as easily as possible. To make it possible, an executable file has been created with the software and all the necessary packages. That means no installation is required for a simple user. You just need to trust the executable file when you are using it.

With a view to reusability and optimization, it is possible to create the executable file from the script following a few steps in the terminal:

### 1. Create the python environment. (if it’s not already done)

> python -m venv venv

2. Enter into the python environment.

> .\venv\Scripts\activate

3. Install pyinstaller.

> pip install pyinstaller

4. Install all the necessary libraries.

> pip install -r requirements.txt

### 5. Get the path of the customtkinter library

> pip show customtkinter

6. Create the .exe file with option to add the assets folder and the necessary customtkinter theme
> | pyinstaller | --onefile | --windowed | --add-data | "<Path | of | the | customtkinter
library>/customtkinter;customtkinter/" main.py

Then the main.exe is created in the dist folder.

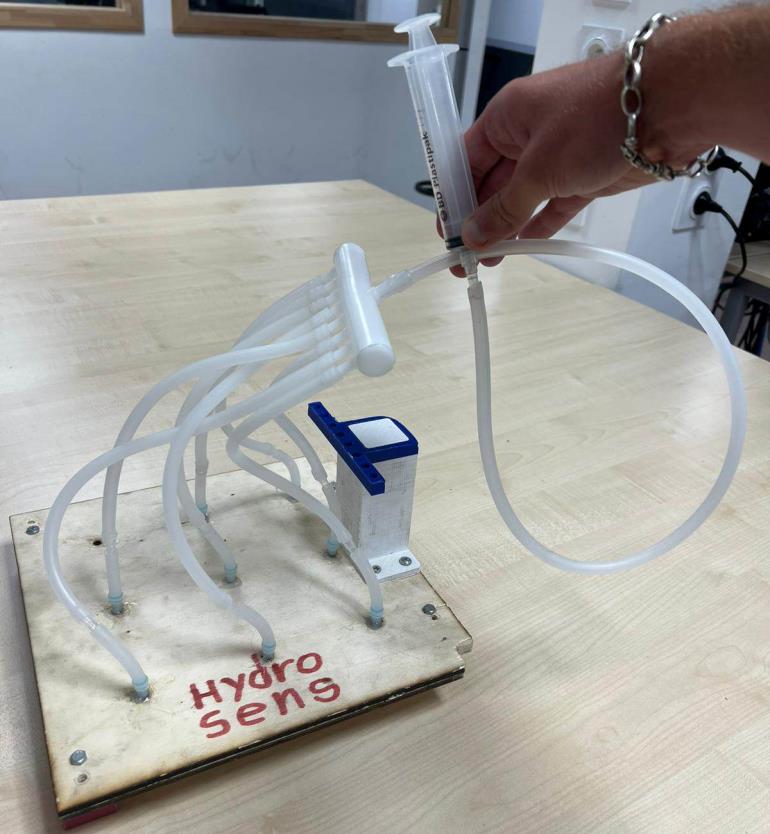
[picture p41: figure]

GROEN JOSHUA, MICHELENA TRISTAN, ROLLAND MELVYN,

## How to prepare the samples

To prepare the samples, follow these steps:

Place the samples on the grid. Note that there are only 8 samples, so the first position on the grid will not have space for a sample.

Once the samples are in place, position the droplet dispenser. To do this correctly, place the dispenser's legs on top of the screws protruding from the ground. Push the entire system against the wall.

Ensure that the tubes protruding from the tube splitter are not connected to any needles.

Attach the precision pipet to the 100ml setting by screwing the cap to either 099 or 100, as shown in the image. Place the plastic cover underneath the syringe's output.

Use the syringe to fill the needles with water. Do this by putting droplets of water into the tubes sticking out of the needles.

Next, connect the tubes sticking out of the tube splitter to the needles.

Once everything is properly attached, you can release the droplets by allowing air to flow through the long tube attached to the upper part of the droplet dispenser.

Once all the droplets are dropped on the paper, please remove the droplet dispenser, and start the image capture with the software.

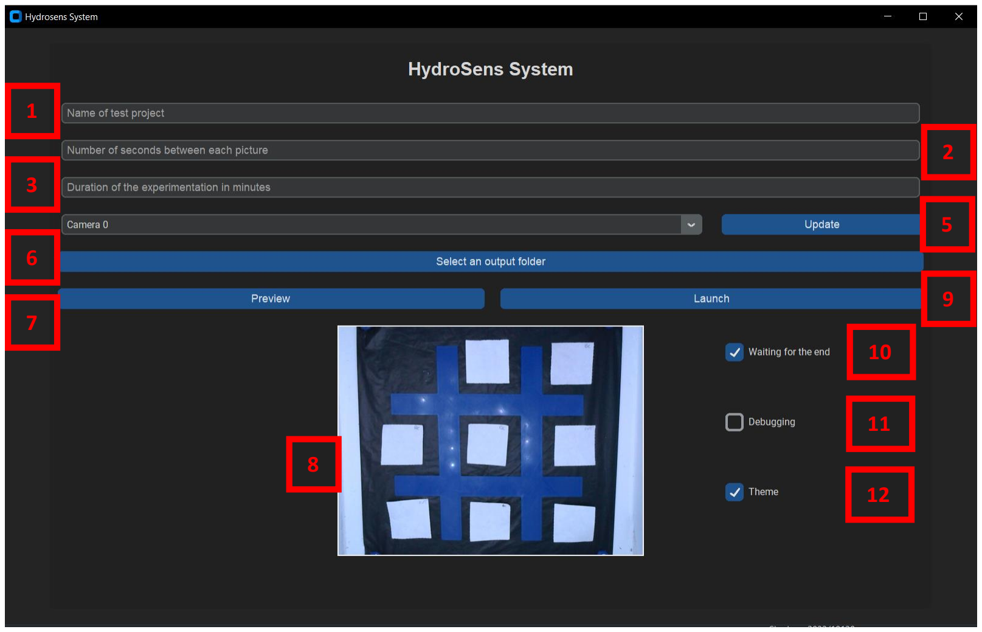
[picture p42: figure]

GROEN JOSHUA, MICHELENA TRISTAN, ROLLAND MELVYN,

## How to use the software

The software release is in an .exe format it is compatible with windows 7, 8, 10 and 11. No prerequisite is needed. When you open the software, a temporary folder called HydroSens_temp will be created, the folder can be deleted after the execution.

The software can run even without the photobox connected. However, to capture pictures using the photobox as intended, please follow these steps:

1 - Connect the photobox to your computer via USB.

2 - Plug in the power plug of the photobox to activate the LEDs.

After opening the software, make sure to select the photobox webcam to ensure the correct device is used for capturing pictures. Use the preview button to check if you have selected the right camera. If the computer does not detect the webcam, please click on the update button.

number | Name of the action | What does it do
1 | Name of test project | Enter the name of the project
2 | Number of seconds between each picture | Define the number of seconds between each picture
3 | Duration of the experiment in minutes | Enter the number of minutes of the duration of the experiment.

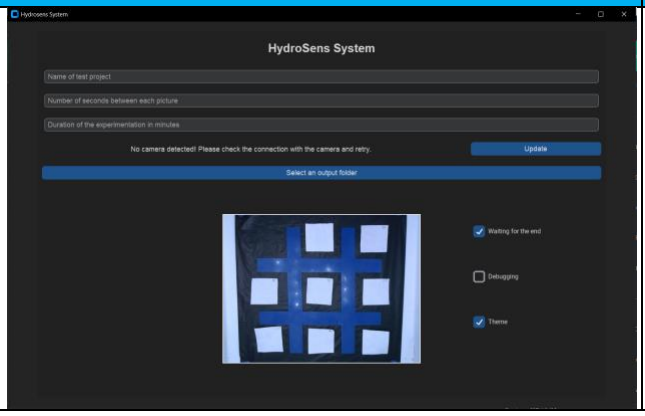
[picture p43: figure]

GROEN JOSHUA, MICHELENA TRISTAN, ROLLAND MELVYN,

4 | Camera selection | Select the camera or webcam if you have multiple devices connected to your computer
5 Update | | Click here to update the list of cameras, if your computer doesn’t find the webcam please verify the webcam is plugged and click on the update button.
6 | Select an output folder | Select a folder where the software will output the results (pictures + .txt file + csv file)
7 | Preview | The preview button takes a picture with the selected webcam for you to check the pictures you will be taking during the experiment. They will be shown in the preview screen.

8 Preview screen

9 | Launch | Launch the image capture.
10 Waiting for the end | | By default, the option is activated that means that the program will go to the end of the parameters given by the user. In the other case it stops the execution when each sample has absorbed water.
11 Debugging | | Show all the pictures and the steps of the image analysis in order to check if something goes wrong or unintended results.
12 | Theme | Change the Theme form Dark Mode (checked) To light mode (unchecked)

Screenshot of the software when no camera is
detected

Screenshot of the software in Light mode

## Conclusion

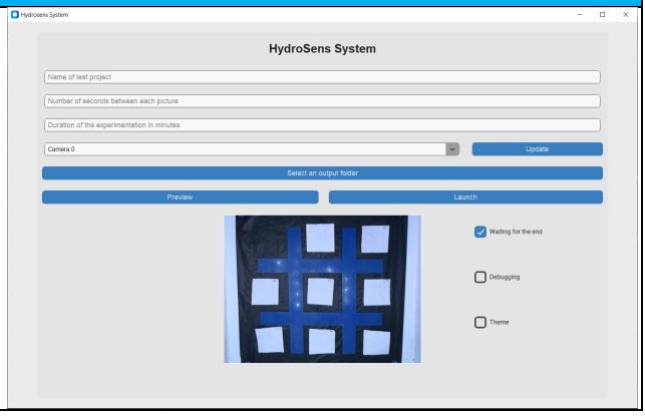
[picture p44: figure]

I hope you find both this manual and the project itself useful. They were specifically designed with the intention of being helpful.

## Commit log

2023-02-17 bill of materials in the making
    [billofmaterials.xlsx]
2023-02-28 box modified
    [AssembledMK1.CATProduct, Door.CATPart, DoorAssembled.CATProduct, DoorKnob.CATPart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]
2023-03-01 Cad Modified
    [back.CATPart, back.stl]
2023-03-02 files for laser cutter added
    [Door.stl, reversible_hinge_with_holes.stl]
2023-03-09 New interface
    The brand new interface is here, very simple and user friendly.
    The main framework is built.
2023-03-11 Camera choice
    Implementation of the choice of the camera in the GUI.
2023-03-17 Ljoint added
    [L joint.CATPart, L joint.stl, foot.stl]
2023-03-24 Update for everyone.
    [billofmaterials.xlsx, budget droplet dispenser.xlsx]
2023-03-24 Add your link in the excel /Notes/Hydrosens-link
    [Hydrosens-link.xlsx]
2023-03-24 Link of KANBAN in excel
    [billofmaterials.xlsx, budget droplet dispenser.xlsx]
2023-03-24 kanban link in excel
    [Hydrosens-link.xlsx]
2023-03-24 Monitoring link
    [Hydrosens-link.xlsx]
2023-03-30 joint V2 added
    [L joint V2.stl, L joint.CATPart]
2023-03-30 Implementation of the interface
    Addition of all the necessary function to take a picture, manage cameras and the user experience.
2023-04-02 Camera function solving error
2023-04-14 modified files
    [Webcam_Connector.stl]
2023-05-05 Create hinge cale.stl
    [hinge cale.stl]
2023-05-16 Automatic detection prototype
2023-05-16 sac poubelle holder added
    [Sac_Poubelle_Retainer.CATPart, Sac_Poubelle_Retainer.stl]
2023-05-19 Create paper holder taged 1.stl
    [paper holder taged 1.stl]
2023-05-22 photobox updated
    [Sac_Poubelle_Retainer.CATPart, Sac_Poubelle_Retainer_bigger.stl]
2023-05-26 magnet holder
    [magnetholder.CATPart, magnetholder.stl, magnetholder2.stl]
2023-06-02 grid added
    [grid.CATPart, grid.stl]
2023-06-02 grit cut in 4 parts
    [grid.CATPart, grid_cut.stl]
2023-06-07 new grid added
    [grid.CATPart, grid_cutbetter.stl]
2023-06-09 New features
    Patch for the detection problem
    Automatization of the text file writer
    Implementation of the samples sort
2023-06-14 Big commit everything change
    [AssembledMK1.CATProduct, Door.CATPart, Door.stl, DoorAssembled.CATProduct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]
2023-06-14 Organization update
    [billofmaterials.xlsx]
